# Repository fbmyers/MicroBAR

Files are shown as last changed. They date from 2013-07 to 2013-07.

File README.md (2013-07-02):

MicroBAR
========

This repository contains hardware, firmware, and software revisions to the Microfluidic Bioamplification Reader (MicroBAR) from UC Berkeley.

githalytics.com alpha githalytics.com (http://githalytics.com/fbmyers/MicroBAR)

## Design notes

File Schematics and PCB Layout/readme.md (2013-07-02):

Schematics and PCB Layout
========

Schematic and PCB layout was done in Altium Designer Release 10.

The MicroBAR consists of two PCBs which are stacked on top of one another.  A single header connects these two boards.  "LAMP Microcontroller PCB" contains the microcontroller and all digital electronics, and it sits on the bottom.  "LAMP Chip PCB" contains the phototransistors, amplifier, MUXes, LED driver, and heater driver.  It sits on top.

Board Level Modifications (to be rolled into next revision):
1) A jumper wire was added between 3 and 6 on U4
2) A jumper wire was added between pin 17 on the expansion header and pin 10 on the B2B header
3) Only 3 LEDs were used along the top side of the detection region (the original plans call for 3 on top and 3 on bottom).

There are a number of problems with the SD card wiring:
4) A jumper wire was added between ICSP1 pin 3 and R1 (SD_SCK)
5) A jumper wire was added between ICSP1 pin 4 and R2 (SD_MOSI)
6) A jumper wire was added between ICSP1 pin 1 and U1 pin 25 (SD_MSIO)
7) Pins 1-3 on the SD slot header were wired incorrectly.  To fix this, the CS line going to pin 2 was jumpered to pin 1 and the original trace going to pin 2 was cut.  The MOSI line going to pin 3 was jumpered to pin 2 and the original trace going to pin 3 was cut.  And pin 3 was jumpered to ground.

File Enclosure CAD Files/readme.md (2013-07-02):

Enclosure CAD Files
========

The enclosure was designed in Rhinocerous 4, exported to STL, and printed on a ZPrint 3D printer.

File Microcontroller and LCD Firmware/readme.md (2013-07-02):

Microcontroller and LCD Firmware
========

Firmware is based on the Arduino 1.0.4 Platform.  The "controller.ino" is the main sketch.  The MicroBAR hardware is based on the Arduino Mega 2560 platform.  The LCD is the Amulet MK-480272C color touchscreen LCD module, which itself features a built-in graphics environment that is programmed with modified HTML/CSS/Javascript.  The Amulet GEMcompiler 1.1.2 was used to compile the HTML files and download them onto the LCD module.

The Atmega 2560 chip must first be programmed with the Arduino Bootloader and the Atmega 8U2 must be programmed with the DFU USB firmware (both using the ICSP headers on the board and an AVR-ISP module).  Then the system will behave as an Arduino and the firmware sketches may be uploaded via USB.  A customized DFU firmware (which identifies itself as "Berkeley MicroBAR 2", rather than "Arduino Mega 2560", is available here.  The bootloader can be installed via the Arduino IDE.

Note that not all hardware features are currently implemented in firmware.

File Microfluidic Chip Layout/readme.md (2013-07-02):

Microfluidic Chip Layout
========

The microfluidic chip was designed in AutoCAD 2012.  Darkfield mylar transparencies were printed (from Fineline Imaging) and SU8/silicon molds were fabricated using standard techniques.  The chamber height (circles) was 200 um while the channel height was 10 um.  The PDMS was poured to a height of 4mm.  See the supplementary info in the PLOS ONE paper for more fabrication details.

This version of the microfluidic disposable cartridge features reaction chambers that are 2mm in diameter.  Although we use 2mm chambers in the paper, 1.5mm would probably be sufficient and would load much faster.  Note that the pitch of the chip is 4.5mm (same as a 384 well plate).

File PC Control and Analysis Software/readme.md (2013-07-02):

PC Control and Analysis Software
========

The Processing UI is based on processing-1.2.1.  This is the main control software for the MicroBAR, and it exposes all of the MicroBAR's current functionality (the LCD UI is not fully-functional).

The Windows driver is identical to the Arduino Mega 2560 driver except the device name has been changed.  

The MATLAB Analysis Scripts parse the log files generated by the Arduino, perform background subtraction and smoothing functions, and generate output graphs.  Future versions of this should combine the MATLAB functionality into the control UI.

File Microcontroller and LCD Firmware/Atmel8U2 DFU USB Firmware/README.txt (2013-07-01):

Arduino Uno and Mega 2560 Firmwares for the ATmega8U2

This directory contains the firmwares used on the ATmega8U2 on the Arduino
Uno and Arduino Mega 2560.  The arduino-usbdfu directory contains the DFU
bootloader on the 8U2; the arduino-usbserial directory contains the actual
usb to serial firmware.  Both should be compiled against LUFA 100807.  The
two .hex files in this directory combine the dfu and serial firmwares into
a single file to burn onto the 8U2.  

To burn (Uno):

avrdude -p at90usb82 -F -P usb -c avrispmkii -U flash:w:UNO-dfu_and_usbserial_combined.hex -U lfuse:w:0xFF:m -U hfuse:w:0xD9:m -U efuse:w:0xF4:m -U lock:w:0x0F:m

To burn (Mega 2560):

avrdude -p at90usb82 -F -P usb -c avrispmkii -U flash:w:MEGA-dfu_and_usbserial_combined.hex -U lfuse:w:0xFF:m -U hfuse:w:0xD9:m -U efuse:w:0xF4:m -U lock:w:0x0F:m

(note: MicroBAR-dfu_and_usbserial_combined.hex is exactly the same as MEGA except the name has been changed to "Berkeley MicroBAR 2")

Note on USB Vendor IDs (VID) and Product IDs (PID): The arduino-usbdfu
project uses Atmel's VID and MCU-specific PIDs to maintain compatibility
with their FLIP software.  The source code to the arduino-usbserial
project includes Atmel's VID and a PID donated by them to LUFA.  This
PID is used in LUFA's USBtoSerial project, which forms the basis for
arduino-usbserial.  According to the LUFA documentation, this VID/PID
combination is:

 "For use in testing of LUFA powered devices during development only,
 by non-commercial entities. All devices must accept collisions on this
 VID/PID range (from other in-development LUFA devices) to be resolved
 by using a unique release number in the Device Descriptor. No devices
 using this VID/PID combination may be released to the general public."

The production version of the arduino-usbserial firmware uses the
Arduino VID.  This is only for use with official Arduino hardware and
should not be used on other products.

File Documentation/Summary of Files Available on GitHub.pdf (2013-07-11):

Rev. 2013-06-21

The GitHub repository contains all of the design and source code files for the MicroBAR in their native format. These include:

Schematics and PCB Layout
Software: Altium Designer 10
1. LAMP Chip PCB.PrjPCB
2. LAMP Microcontroller PCB.PrjPCB

This folder includes two separate projects for the two boards in the MicroBAR:

Microcontroller and LCD Firmware
Software: Adruino 1.0.4 and Amulet Technologies GEMcompiler 1.1.2.
1. Amulet LCD GUI. The "mainmenu.htm" is the root page that should be downloaded to the LCD. Atmel8U2 DFU USB Firmware. This should be programmed onto the 8U2 USB interface chip via AVR-ISP.

2.

Arduino Sketches. These include the firmware code for the MicroBAR. The "controller.ino" is the root sketch. Code for hardware peripherals (LCD, Header, Lights, GPS, etc.) is included in separate sketch files.

3.

This folder includes:

Enclosure CAD Files
Software: Rhinoceros 4
This folder includes the original enclosure design (enclosure.3dm) as well as exported STL files for 3D printing.

PC Control and Analysis Software
Software: Processing 1.2.1 and MATLAB

Windows Driver. Once the 8U2 firmware is loaded, Windows will be able to use this driver to communicate with the MicroBAR as a serial port.

1.

Processing UI. This is the main control program for the MicroBAR, written in the Processing language. LAMP_UI.pde is the main file.

2.

MATLAB Analysis Scripts. All analysis and data visualizationwas carried out in MATLAB. plot_data_from_log.m parses log files generated by the Processing UI and generates a series of plots. microbar_calibration.mat includes the sensitivity coefficient matrix for the detector array.

3.

This folder includes:

Microfluidic Chip Layout
Software: AutoCAD 2012
This folder includes the standard chip layout that we use in this manuscript, which features 96 reaction wells at 4.5 mm pitch, with 16 wells connected in parallel to each of 6 inlets.

## Summary of Files Available on GitHub

LAMP Chip Page 1

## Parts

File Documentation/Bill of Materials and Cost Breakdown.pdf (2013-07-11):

System | Board | Designator | Qty | Vendor | Part # | Mfg # | Description | Function | Unit Price (proto) | Unit Price (>5000) | Ext Price (proto) | Ext price (>5000)
ITO Heater | Top | U1 | 1 Digikey | CLA324-ND | LCA717S | RELAY OPTOMOS 2A SPST-NO 6-SMD | Heater Relay | 6.18 | 2.575 | 6.18 | 2.575
ITO Heater | Top | U7 | 1 Digikey | 296-23551-1-ND | TPS61085PWR IC STEP-UP DC-DC CONV 8-TSSOP | Heater boost converter | 3.33 | 1.283 | 3.33 | 1.283
ITO Heater | Top | C9,C11,C12 | 3 Digikey | 10uF (1206) | input/output filter caps | 0.15 | 0.02 | 0.45 | 0.06
ITO Heater | Top | C10 | 1 Digikey | 1uF (1206) | output filter cap | 0.15 | 0.02 | 0.15 | 0.02
ITO Heater | Top | C13 | 1 Digikey | 100nF (1206) | 0.15 | 0.02 | 0.15 | 0.02
ITO Heater | Top | C14 | 1 Digikey | 2.2nF (1206) | 0.15 | 0.02 | 0.15 | 0.02
ITO Heater | Top | R4 | 1 Digikey | 150k (1206) | 0.05 | 0.01 | 0.05 | 0.01
ITO Heater | Top | R5 | 1 Digikey | 18.2k (1206) | 0.05 | 0.01 | 0.05 | 0.01
ITO Heater | Top | R6 | 1 Digikey | 15k (1206) | 0.05 | 0.01 | 0.05 | 0.01
ITO Heater | Top | R7 | 1 Digikey | 1k (1206) | Half bridge for thermistor | 0.05 | 0.01 | 0.05 | 0.01
ITO Heater | Top | L3 | 1 Digikey | 490-5270-1-ND | LQH55PN6R8NR0LINDUCTOR POWER 6.8UH 1450MA 2220 | 6.8uH heater inductor | 0.44 | 0.172 | 0.44 | 0.172
ITO Heater | Top | D97 | 1 Digikey | 641-1255-1-ND | CDBA120SL-G | DIODE SCHOTTKY 1A 20V SMA | heater diode | 0.82 | 0.209 | 0.82 | 0.209
ITO Heater | Top | RT1 | 1 Digikey | 615-1043-ND | PPG102A1RD | DETECTOR RTD TF 1K OHM +/-0.06% | Thermistor | 18.5 | 2.06 | 18.5 | 2.06
ITO Heater | Top | RT1 | 1 Digikey | 455-1719-ND | S2B-PH-K-S(LF)(SN) CONN HEADER PH SIDE 2POS 2MM | header for thermistor | 0.1 | 0.047 | 0.1 | 0.047
ITO Heater | Top | RT1 | 1 Digikey | 455-1165-ND | PHR-2 | CONN HOUSING PH 2POS 2MM WHITE | 2-pin housing for thermistor | 0.05 | 0.024 | 0.05 | 0.024
ITO Heater | Top | RT1 | 2 Digikey | 455-2148-1-ND | SPH-002T-P0.5L CONN TERMINAL 28-24AWG TIN | JST PH pins | 0.027 | 0.013 | 0.054 | 0.026
ITO Heater | Top | RT1 | 1 Digikey | MC06G-300-ND | 3365/06 300SF CABLE 6 COND 300FT FLAT GRAY | 2-conductor ribbon cable (3 inches) | 0.01 | 0.01 | 0.01 | 0.01
ITO Heater | Top | 1 Delta Tech | CB-50IN-S205 | CB-50IN-S205 | 5-15 ohm, 50x75x0.5mm ITO slides | Heater | 20 | 5 | 20 | 5
ITO Heater | Top | 1 Ace HW | Brass Bar Stock | Heater Contacts | 0.5 | 0.25 | 0.5 | 0.25
ITO Heater | Top | 1 Fry's | Electrically-conductive Epoxy | Heater Contacts | 0.2 | 0.1 | 0.2 | 0.1
ITO Heater | Top | 1 Ace HW | Thermally-conductive Epoxy | Glue for Thermistor | 0.05 | 0.05 | 0
TOTAL: | 51.334 | 11.916
LED Driver | Top | U6 | 1 Digikey | 576-3041-1-ND | MIC3289-24YD6 TRIC LED DRIVR WHITE BCKLGT TSOT-6 | LED booster | 1.9 | 0.973 | 1.9 | 0.973
LED Driver | Top | C6 | 1 Digikey | 10uF (1206) | 0.15 | 0.02 | 0.15 | 0.02
LED Driver | Top | C7 | 1 Digikey | 1uF (1206) | 0.15 | 0.02 | 0.15 | 0.02
LED Driver | Top | C8 | 1 Digikey | 478-6028-1-ND | 06033D334KAT2ACAP CER .33UF 25V X5R 0603 (sub w/ 1206) | 0.33uF | 0.45 | 0.126 | 0.45 | 0.126
LED Driver | Top | R3 | 1 Digikey | P12.4CCT-ND | ERJ-6ENF12R4V RES 12.4 OHM 1/8W 1% 0805 SMD | current sense resistor | 0.07 | 0.005 | 0.07 | 0.005
LED Driver | Top | L2 | 1 Digikey | 490-5271-1-ND | LQH55PN100MR0LINDUCTOR POWER 10UH 1250MA 2220 | 10uH LED inductor | 0.44 | 0.172 | 0.44 | 0.172
LED Driver | Top | P3 | 1 Digikey | 455-1719-ND | S2B-PH-K-S(LF)(SN) CONN HEADER PH SIDE 2POS 2MM | header for leds | 0.1 | 0.047 | 0.1 | 0.047
LED Driver | Top | P3 | 1 Digikey | 455-1165-ND | PHR-2 | CONN HOUSING PH 2POS 2MM WHITE | 2-pin housing for leds | 0.05 | 0.024 | 0.05 | 0.024
LED Driver | Top | P3 | 2 Digikey | 455-2148-1-ND | SPH-002T-P0.5L CONN TERMINAL 28-24AWG TIN | JST PH pins | 0.027 | 0.013 | 0.054 | 0.026
LED Driver | Top | P3 | 1 Digikey | MC06G-300-ND | 3365/06 300SF CABLE 6 COND 300FT FLAT GRAY | 2-conductor ribbon cable (3 inches) | 0.01 | 0.01 | 0.01 | 0.01
LED Driver | Top | P3 | 3 Digikey | P14150CT-ND | LNJ923W8CRA1 LED BLUE SIDE VIEW SMD | Blue LEDs | 0.57 | 0.229 | 1.71 | 0.687
LED Driver | Top | 1 Ace HW | Liquid Electrical Tape | Optical shielding | 0.05 | 0.02 | 0.05 | 0.02
TOTAL: | 5.134 | 2.13
Phototransistor Array | Top | D1-D96 | 96 Digikey | 475-1268-1-ND | SFH 3710-3/4-Z PHOTOTRANSISTOR ALS SMD CHIPLED | Phototransistors | 0.563 | 0.483 | 54.048 | 46.368
Phototransistor Array | Top | U2,U4,U5 | 3 Digikey | ADG732BSUZ-ND | ADG732BSUZ | IC MULTIPLEXER 32X1 48TQFP | MUXes | 12.13 | 6.062 | 36.39 | 18.186
Phototransistor Array | Top | U3 | 1 Digikey | AD8603AUJZREEL7CT-NDAD8603AUJZ-REEL7IC OPAMP GP R-R CMOS TSOT23-5 | transimpedance opamp | 2.07 | 0.797 | 2.07 | 0.797
Phototransistor Array | Top | C4 | 1 Digikey | 10pF | fb capacitor | 0.15 | 0.02 | 0.15 | 0.02
Phototransistor Array | Top | C5 | 1 Digikey | 10pF - not necessary? | input capacitor | 0 | 0 | 0 | 0
Phototransistor Array | Top | R1 | 1 Digikey | 1M | fb resistor | 0.1 | 0.01 | 0.1 | 0.01
Phototransistor Array | Top | R2 | 1 Digikey | 1G - not necessary? | input resistor | 0 | 0 | 0 | 0
Phototransistor Array | Top | R100-101 | 2 Digikey | 1M | bias resistors | 0.1 | 0.01 | 0.2 | 0.02
Phototransistor Array | Top | 1 McMaster | 8647K108 | Neoprene/EPDM/SBR, Soft, 1/16" Thick, 42" Width | black foam | 0.04 | 0.04 | 0.04 | 0.04
Phototransistor Array | Top | 1 McMaster | 7769T88 (#89) | Light Filters 20" X 24" Sheet | "Moss Green" gel #89 | 0.16 | 0.16 | 0.16 | 0.16
TOTAL: | 93.158 | 65.601
Microcontroller | Bot | U1 | 1 Digikey | ATMEGA2560-16AU-NDATMEGA2560-16AUIC AVR MCU 256K 16MHZ 100TQFP | microcontroller | 17.97 | 11.251 | 17.97 | 11.251
Microcontroller | Bot | C1 | 1 Digikey | 22pF (1206) | cap on reset line | 0.15 | 0.02 | 0.15 | 0.02
Microcontroller | Bot | C2-3 | 2 Digikey | 478-3735-1-ND | 08051A200JAT2ACAP CERM 20PF 5% 100V NP0 0805 | xtal caps | 0.23 | 0.038 | 0.46 | 0.076
Microcontroller | Bot | C4-7 | 4 Digikey | 100nF (1206) | decoupling caps | 0.15 | 0.02 | 0.6 | 0.08
Microcontroller | Bot | R4 | 1 Digikey | 10k (1206) | res on reset line | 0.1 | 0.01 | 0.1 | 0.01
Microcontroller | Bot | R8 | 1 Digikey | 1M (1206) | res on xtal | 0.1 | 0.01 | 0.1 | 0.01
Microcontroller | Bot | R11 | 1 Digikey | 27 ohm (1206) | res on xtal | 0.1 | 0.01 | 0.1 | 0.01
Microcontroller | Bot | Y1 | 1 Digikey | XC1282CT-ND | ECS-160-20-5PX-TRCRYSTAL 16.00MHZ 20PF SMD | xtal | 0.56 | 0.25 | 0.56 | 0.25
Microcontroller | Bot | R9-10 | 2 Digikey | 10k (1206) | pullups on PD1/PD0 | 0.1 | 0.01 | 0.2 | 0.02
Microcontroller | Bot | P1 | 1 Digikey | 609-3218-ND | 67996-406HLF | CONN HEADER 6POS .100 STR TIN | ICSP1 header | 0.43 | 0 | 0.43 | 0
TOTAL: | 20.67 | 11.727
USB Interface | Bot | U5 | 1 Digikey | ATMEGA8U2-AU-ND | ATMega8U2-AU MCU AVR 8K FLASH 16MHZ 32TQFP | usb controller | 3.7 | 2.352 | 3.7 | 2.352
USB Interface | Bot | C16-17 | 2 Digikey | 478-3735-1-ND | 08051A200JAT2ACAP CERM 20PF 5% 100V NP0 0805 | xtal caps | 0.23 | 0.038 | 0.46 | 0.076
USB Interface | Bot | R25 | 1 Digikey | 1M (1206) | res on xtal | 0.1 | 0.01 | 0.1 | 0.01
USB Interface | Bot | R26 | 1 Digikey | 27 ohm (1206) | res on xtal | 0.1 | 0.01 | 0.1 | 0.01
USB Interface | Bot | Y2 | 1 Digikey | XC1282CT-ND | ECS-160-20-5PX-TRCRYSTAL 16.00MHZ 20PF SMD | xtal | 0.56 | 0.25 | 0.56 | 0.25
USB Interface | Bot | R24 | 1 Digikey | 10k (1206) | pullup on reset line | 0.1 | 0.01 | 0.1 | 0.01
USB Interface | Bot | R29-30 | 2 Digikey | 22 ohm (1206) | USB data line resistors | 0.1 | 0.01 | 0.2 | 0.02
USB Interface | Bot | Z1-2 | 2 Digikey | F2594CT-ND | PGB1010603MR SUPPRESSOR ESD 24VDC 0603 SMD | USB data line ESD protection | 0.74 | 0.196 | 1.48 | 0.392
USB Interface | Bot | L2 | 1 Digikey | 490-1038-1-ND | BLM21AG121SN1DFERRITE CHIP 120 OHM 200MA 0805 | ESD protection inductor | 0.33 | 0.039 | 0.33 | 0.039
USB Interface | Bot | P10 | 1 Digikey | 609-1039-ND | 61729-0010BLF CONN RCPT USB TYPE B R/A PCB | USB-B port | 1.29 | 0.474 | 1.29 | 0.474
USB Interface | Bot | C18 | 1 Digikey | 100nF (1206) | 0.15 | 0.01 | 0.15 | 0.01
USB Interface | Bot | C19 | 1 Digikey | 1uF (1206) | 0.15 | 0.01 | 0.15 | 0.01
USB Interface | Bot | R27-28 | 2 Digikey | 1k (1206) | TX/RX pullups | 0.1 | 0 | 0.2 | 0
USB Interface | Bot | D7-8 | 2 Digikey | 67-1046-ND | SSL-LX2573GD | LED 2X5MM RECTANGULAR GREEN DIFF | TX/RX LEDs | 0.37 | 0 | 0.74 | 0
USB Interface | Bot | R31-32 | 2 Digikey | 1k (1206) | data line resistors | 0.1 | 0.01 | 0.2 | 0.02
USB Interface | Bot | C20 | 1 Digikey | 100nF (1206) | reset DTR line cap | 0.15 | 0.02 | 0.15 | 0.02
USB Interface | Bot | P8 | 1 Digikey | 609-3218-ND | 67996-406HLF | CONN HEADER 6POS .100 STR TIN | ICSP2 header | 0.43 | 0 | 0.43 | 0
USB Interface | 1 Digikey | Q361-ND | 3021001-03 | CBL USB A-B CON 3' 28/28 AWG | 3' USB cable | 3.15 | 1.23 | 3.15 | 1.23
TOTAL: | 13.49 | 4.923
SD Card Reader | Bot | P9 | 1 Digikey | 478-5063-1-ND | 145738009302859+CONNECTOR SD CARD W/BOSS | SD card slot | 4.7 | 2.916 | 4.7 | 2.916
SD Card Reader | Bot | R33-34 | 2 Digikey | 10k (1206) | card detect / write protect pullups | 0.1 | 0.01 | 0.2 | 0.02
SD Card Reader | Bot | R1-3 | 3 Digikey | 1.8k (1206) | SD level shifter res | 0.1 | 0.01 | 0.3 | 0.03
SD Card Reader | Bot | R5-7 | 3 Digikey | 3.3k (1206) | SD level shifter res | 0.1 | 0.01 | 0.3 | 0.03
SD Card Reader | Bot | U3 | 1 Digikey | 296-18479-1-ND | LP2985A-33DBVRIC LDO REG 3.3V 150MA SOT23-5 | 3.3V regulator | 0.84 | 0.276 | 0.84 | 0.276
SD Card Reader | Bot | C12 | 1 Digikey | 1uF (1206) | input cap for 3.3v reg | 0.15 | 0.02 | 0.15 | 0.02
SD Card Reader | Bot | C13 | 1 Digikey | 2.2uF(1206) | output cap for 3.3v reg | 0.15 | 0.02 | 0.15 | 0.02
SD Card Reader | 1 Amazon | 512MB SD Card | 6 | 3 | 6 | 3
TOTAL: | 12.64 | 6.312
Cell Module | Bot | P11 | 1 Digikey | 255-2997-1-ND | AXK5F60547YG CONN SOCKET BRD/BRD .5MM 60POS | 60-pin socket for cell module | 6.79 | 3.514 | 6.79 | 3.514
Cell Module | Bot | P12 | 1 Digikey | WM3291CT-ND | 473880001 1.90MM SIM CARD READER CONN | SIM card socket | 1.51 | 0.986 | 1.51 | 0.986
Cell Module | Bot | U6 | 1 Digikey | 1016-1243-5-ND | SPX29302T5-L | IC REG LDO ADJ 3A TO263-5 | 3.8V 3A regulator | 2.68 | 1.123 | 2.68 | 1.123
Cell Module | Bot | R15 | 1 Digikey | 22k | 3.8V voltage set res | 0.1 | 0.01 | 0.1 | 0.01
Cell Module | Bot | R16 | 1 Digikey | 10k | 3.8V voltage set res | 0.1 | 0.01 | 0.1 | 0.01
Cell Module | Bot | C8 | 1 Digikey | 478-1777-1-ND | TPSD107K010R0100 CAP TANT LOESR 100UF 10V 10% SMD | output cap for 3.8V reg | 1.13 | 0.36 | 1.13 | 0.36
Cell Module | Bot | C9 | 1 Digikey | 0.1uF | output cap for 3.8V reg | 0.15 | 0.02 | 0.15 | 0.02
Cell Module | Bot | R17 | 1 Digikey | 10k | pullup for boot res | 0.1 | 0.01 | 0.1 | 0.01
Cell Module | Bot | P7 | 1 Digikey | 455-1722-ND | S5B-PH-K-S(LF)(SN) CONN HEADER PH SIDE 5POS 2MM | 5-pin JST PH header for cell phone spkr/mic | 0.2 | 0 | 0.2 | 0
Cell Module | Bot | 1 Digikey | 455-1163-ND | PHR-5 | CONN HOUSING PH 5POS 2MM WHITE | 5-pin housing - for mic/spkr cable | 0.07 | 0 | 0.07 | 0
Cell Module | Bot | 1 Sparkfun | CEL-09533 | GSM/GPRS Module - SM5100B | SM5100B Cell Module | 59.95 | 47.96 | 59.95 | 47.96
Cell Module | Bot | 1 Sparkfun | CEL-00675 | Quad-band Cellular Duck Antenna SMA | Cell Antenna | 7.95 | 6.39 | 7.95 | 6.39
Cell Module | Bot | 1 | Prepay SIM card | 0 | 0 | 0 | 0
TOTAL: | 80.73 | 60.383
GPS Module | Bot | P4 | 1 Digikey | 455-1721-ND | S4B-PH-K-S(LF)(SN) CONN HEADER PH SIDE 4POS 2MM | 6-pin JST header for GPS | 0.17 | 0.076 | 0.17 | 0.076
GPS Module | Bot | P4 | 1 Digikey | 455-1396-ND | SHR-06V-S | CONN HOUSING SH 6POS 1MM WHITE | housing for GPS connector | 0.11 | 0.049 | 0.11 | 0.049
GPS Module | Bot | P4 | 6 Digikey | 455-2148-1-ND | SPH-002T-P0.5L CONN TERMINAL 28-24AWG TIN | JST PH pins | 0.027 | 0.013 | 0.162 | 0.078
GPS Module | Bot | P4 | 1 Digikey | MC06G-300-ND | 3365/06 300SF CABLE 6 COND 300FT FLAT GRAY | 6-cond 28 awg ribbon (3 inches) | 0.03 | 0.03 | 0.03 | 0.03
GPS Module | Bot | P4 | 1 Digikey | 455-1396-ND | SHR-06V-S | CONN HOUSING SH 6POS 1MM WHITE | 6-pin JST housing - GPS end | 0.11 | 0.049 | 0.11 | 0.049
GPS Module | Bot | P4 | 1 Digikey | 455-1561-1-ND | SSH-003T-P0.2 CONN TERM SH CRIMP 28-32AWG TIN | JST SH pins | 0.049 | 0.032 | 0.049 | 0.032
GPS Module | 1 Sparkfun | GPS-00465 | 20 Channel EM-406A SiRF III Receiver with Antenna | GPS module | 59.95 | 47.96 | 59.95 | 47.96
TOTAL: | 60.581 | 48.274
5V Power Supply | Bot | U4 | 1 Digikey | LT1308ACS8#PBF-ND LT1308ACS8#PBFIC DC/DC CONV SINGLE CELL 8-SOIC | 5V, 1A regulator | 6.5 | 3.634 | 6.5 | 3.634
5V Power Supply | Bot | C11 | 1 Digikey | 478-3911-1-ND | TAJC476M010RNJCAP TANTALUM 47UF 10V 20% SMD | 5V booster input cap | 0.46 | 0.147 | 0.46 | 0.147
5V Power Supply | Bot | C15 | 1 Digikey | 22nF (1206) | 0.15 | 0.02 | 0.15 | 0.02
5V Power Supply | Bot | C14 | 1 Digikey | 478-3061-1-ND | TPSD227M006R0100 CAP TANT LOESR 220UF 6.3V 20%SMD | 5V booster output cap | 3.5 | 1.12 | 3.5 | 1.12
5V Power Supply | Bot | R23 | 1 Digikey | 47k (1206) | 0.1 | 0.01 | 0.1 | 0.01
5V Power Supply | Bot | R21 | 1 Digikey | 309k (1206) | 0.1 | 0.01 | 0.1 | 0.01
5V Power Supply | Bot | R22 | 1 Digikey | 100k (1206) | 0.1 | 0.01 | 0.1 | 0.01
5V Power Supply | Bot | L1 | 1 Digikey | 490-5269-1-ND | LQH55PN4R7NR0LINDUCTOR POWER 4.7UH 1750MA 2220 | 5V booster inductor | 0.44 | 0.172 | 0.44 | 0.172
5V Power Supply | Bot | D6 | 1 Digikey | 10BQ015PBFCT-ND | 10BQ015TRPBF DIODE SCHOTTKY 15V 1A SMB | 5V booster diode | 1.02 | 0.336 | 1.02 | 0.336
TOTAL: | 12.37 | 5.459
LiPo Battery/USB Charger | Bot | U2 | 1 Digikey | MCP73831T-2ATI/OTCT-ND MCP73831T-2ATI/OT IC CONTROLLR LI-ION 4.2V SOT23-5 | lipo charger | 0.68 | 0.42 | 0.68 | 0.42
LiPo Battery/USB Charger | Bot | D4 | 1 Digikey | 67-1050-ND | SSL-LX2573YD | LED 2X5MM RECTANGULAR YEL DIFF | charging LED (yellow) | 0.28 | 0.08 | 0.28 | 0.08
LiPo Battery/USB Charger | Bot | R19 | 1 Digikey | 1k (1206) | charging LED res | 0.1 | 0.01 | 0.1 | 0.01
LiPo Battery/USB Charger | Bot | R18 | 1 Digikey | 2k (1206) | current selector for charging IC | 0.1 | 0.01 | 0.1 | 0.01
LiPo Battery/USB Charger | Bot | F1 | 1 Digikey | 507-1075-1-ND | C1Q 500 | FUSE 500MA 125V 1206 FAST C1Q | 500mA USB charging fuse | 0.55 | 0.142 | 0.55 | 0.142
LiPo Battery/USB Charger | Bot | F2 | 1 Digikey | 507-1082-1-ND | C1Q 3 | 3A fuse | 3A battery fuse | 0.55 | 0.142 | 0.55 | 0.142
LiPo Battery/USB Charger | Bot | C10 | 1 Digikey | 478-3934-1-ND | TAJD475M035RNJCAP TANTALUM 4.7UF 35V 20% SMD | lipo charger cap | 0.97 | 0.35 | 0.97 | 0.35
LiPo Battery/USB Charger | Bot | P2 | 1 Digikey | 455-1704-ND | B2B-PH-K-S(LF)(SN) CONN HEADER PH TOP 2POS 2MM | battery connector | 0.1 | 0.0476 | 0.1 | 0.0476
LiPo Battery/USB Charger | Bot | P2 | 1 Sparkfun | PRT-08484 | 6Ah LiPo battery w/ JST connector | battery (many options for this) | 39.95 | 31.96 | 39.95 | 31.96
LiPo Battery/USB Charger | Bot | 2 | screws/brackets for mounting battery | 0.1 | 0.1 | 0.2 | 0.2
TOTAL: | 43.48 | 33.3616
Touchscreen LCD | P3 | 1 Digikey | 455-1721-ND | S4B-PH-K-S(LF)(SN) CONN HEADER PH SIDE 4POS 2MM | header for LCD | 0.17 | 0.076 | 0.17 | 0.076
Touchscreen LCD | P3 | 1 Digikey | 455-1164-ND | PHR-4 | CONN HOUSING PH 4POS 2MM WHITE | 4-pin housing | 0.07 | 0.03 | 0.07 | 0.03
Touchscreen LCD | P3 | 4 Digikey | 455-2148-1-ND | SPH-002T-P0.5L CONN TERMINAL 28-24AWG TIN | JST PH pins | 0.027 | 0.013 | 0.108 | 0.052
Touchscreen LCD | P3 | 1 Digikey | MC06G-300-ND | 3365/06 300SF CABLE 6 COND 300FT FLAT GRAY | 4-cond 28 awg ribbon | 0.02 | 0.02 | 0.02 | 0.02
Touchscreen LCD | 1 Digikey | 681-1018-ND | MK-480272C | KIT COLOR MODULE 480X272 TFT | 4.3" Color LCD Touchscreen | 223.44 | 50 | 223.44 | 50
TOTAL: | 223.808 | 50.178
General | Bot | D1,D2 | 2 Digikey | 67-1047-ND | SSL-LX2573ID | LED 2X5MM RECTANGULAR RED DIFF | Status LEDs (red) | 0.37 | 0.079 | 0.74 | 0.158
General | Bot | D5 | 1 Digikey | 67-1046-ND | SSL-LX2573GD | LED 2X5MM RECTANGULAR GREEN DIFF | power LED (grn) | 0.37 | 0.074 | 0.37 | 0.074
General | Bot | R12,R13,R20 | 3 Digikey | 1k (1206) | Resistors for status/power LEDs | 0.1 | 0.01 | 0.3 | 0.03
General | Bot | S1 | 1 Digikey | 401-1223-ND | F2UEE | SWITCH PB DPDT ALT ACT SILVER | power switch | 2.32 | 1.036 | 2.32 | 1.036
General | Bot | S1 | 1 Digikey | 401-1221-ND | F1204 | SW CAP RECT GREY 5.5MM ACT | power switch gray cap | 1.05 | 0.355 | 1.05 | 0.355
General | Bot | B1 | 1 Digikey | 458-1066-ND | PK-12N40PQ | BUZZER PIEZO 4.1KHZ 14MM PC MT | Buzzer | 2.43 | 1.978 | 2.43 | 1.978
General | Bot | P6 | 1 Digikey | WM8129-ND | 90131-0131 | CONN HEADER 22POS .100" STR TIN | 2x11 expansion header | 2.36 | 0 | 2.36 | 0
General | Top | P1 | 1 Digikey | 609-3220-ND | 67996-416HLF | CONN HEADER 16POS .100 STR TIN | 2x8 male board 2 board header | 0.83 | 0.277 | 0.83 | 0.277
General | Bot | P5 | 1 Digikey | WM4241-ND | 901512116 C-GRID PCB CONN DR VT TN-A 16CKT | 2x8 female board 2 board header | 3.24 | 1.484 | 3.24 | 1.484
General | 4 | standoff | standoffs between boards | 0.3 | 0.1 | 1.2 | 0.4
General | 8 | screws for enclosure | 0.02 | 0.005 | 0.16 | 0.04
General | 1 | black foam for optical shielding in lid | 0.04 | 0.04 | 0.04 | 0.04
TOTAL: | 15.04 | 5.872
Manufacturing | 1 Adv. Ckits | PCB Fabrication | 66 | 10 | 66 | 10
Manufacturing | 1 Adv. Ckits | PCB Assembly (SMT soldering) | 130.6 | 53.96 | 130.6 | 53.96
Manufacturing | 1 | 3D printed enclosure (low quant) | 10 | 10 | 0
Manufacturing | 1 QuickParts | Injection molded enclosure (high quant) | 2.5 | 0 | 2.5
Manufacturing | 1 | Assembly & Testing (low quant, 4 hr @ $20/hr) | 80 | 80 | 0
Manufacturing | 1 | Assembly & Testing (high quant, 2hr @ $5/hr) | 10 | 0 | 10
TOTAL: | 286.6 | 76.46
| Prototype | >5000
FULL BOX TOTAL NO LCD/GPS/CELL | 919.035 553.916 | 382.5966 223.7616

## MicroBAR v.2 Bill of Materials

Manufacturing Totals

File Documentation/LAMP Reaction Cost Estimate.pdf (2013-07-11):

Reaction Volume: | 6.28E-07 L
Reaction Cost: | 0.012893607
Cost/uL: | 0.020531221
Cost/chip | 1.237786242

Solids
Reagent | Molecular Weight | Mass (g) | Moles | Cost | Cost/mole | Concentration/Rea | Moles/reaction | Cost/reaction | Fraction of Cost
Tris Buffer | 127.2 | 100 | 0.786163522 | $74 | 94.128 | 0.02 | 1.256E-08 | 1.18225E-06 | 0.01%
KCl | 74.55 | 500 | 6.706908115 | $31 | 4.59228 | 0.01 | 6.28E-09 | 2.88395E-08 | 0.00%
MgSO4.7H2O | 246.47 | 500 | 2.02864446 | $30 | 14.7882 | 0.008 | 5.024E-09 | 7.42959E-08 | 0.00%
(NH4)2SO4 | 132.14 | 100 | 0.756773119 | $14 | 18.76388 | 0.01 | 6.28E-09 | 1.17837E-07 | 0.00%
MnCl2 | 197.91 | 100 | 0.505280178 | $22 | 43.93602 | 0.001 | 6.28E-10 | 2.75918E-08 | 0.00%
Calcein | 622.53 | 5 | 0.008031741 | $103 | 12761.865 | 0.00005 | 3.14E-11 | 4.00723E-07 | 0.00%

Solutions
Reagent | Concentration (M) | Volume (L) | Moles | Cost | Cost/mole | Rxn Concentration | Moles/reaction | Cost/reaction | Fraction of Cost
Betaine | 5 | 0.0015 | 0.0075 | $20 | 2666.666667 | 0.8 | 5.024E-07 | 0.001339733 | 10.39%
dATP | 0.1 | 0.00025 | 0.000025 | $37 | 1470000 | 0.0014 | 8.792E-10 | 0.001292424 | 10.02%
dCTP | 0.1 | 0.00025 | 0.000025 | $37 | 1470000 | 0.0014 | 8.792E-10 | 0.001292424 | 10.02%
dGTP | 0.1 | 0.00025 | 0.000025 | $37 | 1470000 | 0.0014 | 8.792E-10 | 0.001292424 | 10.02%
dTTP | 0.1 | 0.00025 | 0.000025 | $37 | 1470000 | 0.0014 | 8.792E-10 | 0.001292424 | 10.02%
Bst Polymerase | 8000000 | 0.001 | 8000 | $244 | 0.0305 | 320000 | 0.20096 | 0.00612928 | 47.54%
Tween 20 (%) | 1 | 100 | 100 | $27 | 0.273 | 0.2 | 1.256E-07 | 3.42888E-08 | 0.00%
Primers FIP/BIP | | | 0.0000005 | 45 | 90000000 | 0.0000032 | 2.0096E-12 | 0.000180864 | 1.40%
Primers LoopF/B | | | 0.0000002 | 10 | 50000000 | 0.0000016 | 1.0048E-12 | 0.00005024 | 0.39%
Primers F3/B3 | | | 0.0000002 | 16 | 80000000 | 0.0000004 | 2.512E-13 | 0.000020096 | 0.16%

Reagents are from Sigma or New England Biosciences, Primers are from IDT

MicroBAR LAMP Reaction Cost Estimate

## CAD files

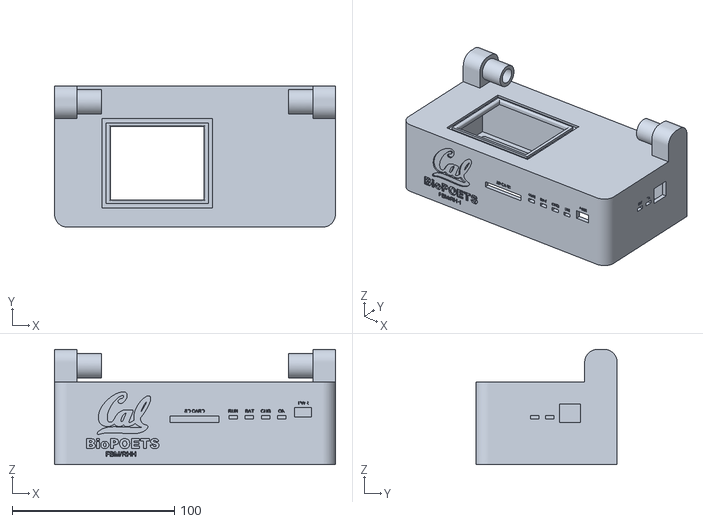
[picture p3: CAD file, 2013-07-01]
Enclosure CAD Files/STL Files/enclosure v1 - body.stl
173.0 x 87.0 x 71.0

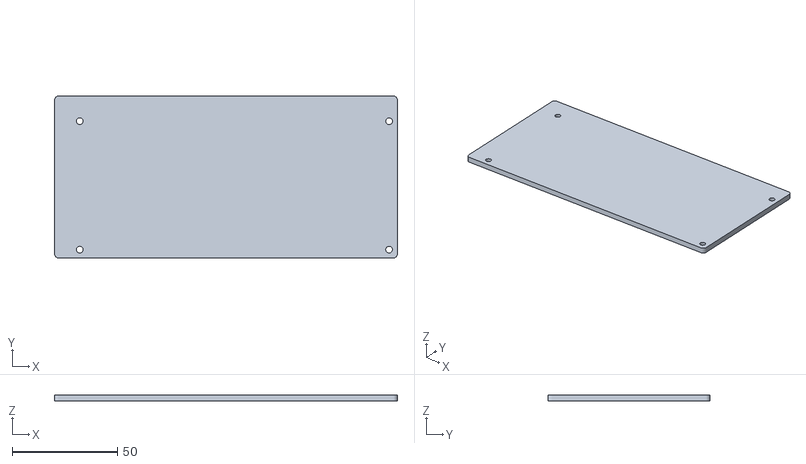
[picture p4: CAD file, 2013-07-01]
Enclosure CAD Files/STL Files/enclosure v1 - bottom plate.stl
163.0 x 77.0 x 3.00

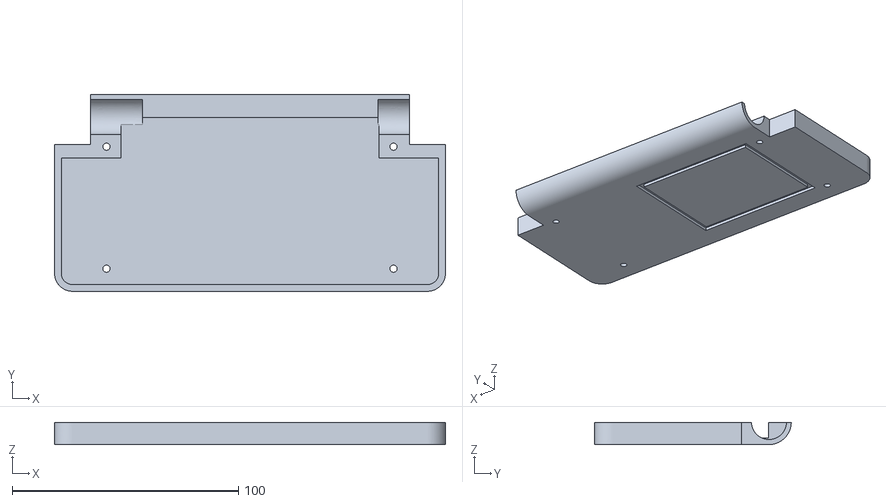
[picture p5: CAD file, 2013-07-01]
Enclosure CAD Files/STL Files/enclosure v1 - lid bottom.stl
173.0 x 87.0 x 9.84

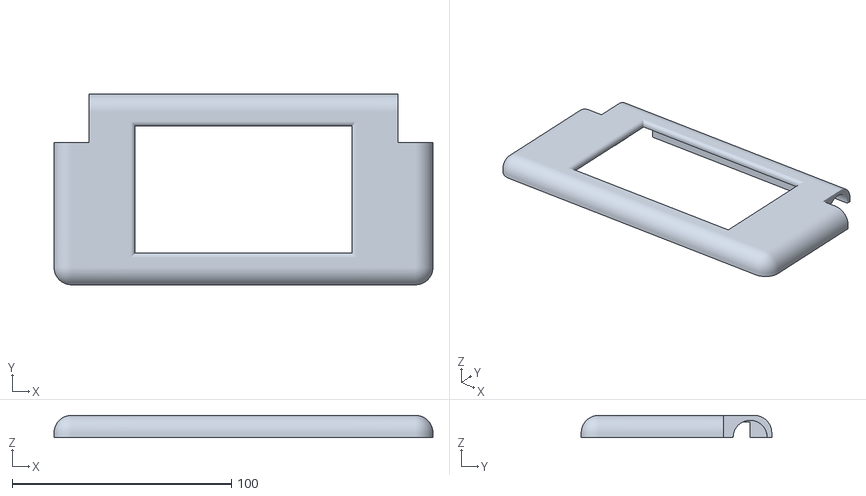
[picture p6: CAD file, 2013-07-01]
Enclosure CAD Files/STL Files/enclosure v1 - lid top.stl
173.0 x 87.0 x 10.2

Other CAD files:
Microfluidic Chip Layout/MicroBAR Chip - 2mm Chambers - V1.dwg
Schematics and PCB Layout/Gerber Files/Chip Reader PCB Top Paste Mask.dxf
Schematics and PCB Layout/Gerber Files/Microcontroller PCB Top Paste Mask.dxf

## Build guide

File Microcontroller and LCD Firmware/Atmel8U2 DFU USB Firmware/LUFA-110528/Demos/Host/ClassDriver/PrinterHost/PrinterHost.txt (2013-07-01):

/** \file
 *
 *  This file contains special DoxyGen information for the generation of the main page and other special
 *  documentation pages. It is not a project source file.
 */

/** \mainpage Printer Host Demo
 *
 *  \section Sec_Compat Demo Compatibility:
 *
 *  The following list indicates what microcontrollers are compatible with this demo.
 *
 *  - Series 7 USB AVRs (AT90USBxxx7)
 *
 *  \section Sec_Info USB Information:
 *
 *  The following table gives a rundown of the USB utilization of this demo.
 *
 *  <table>
 *   <tr>
 *    <td><b>USB Mode:</b></td>
 *    <td>Host</td>
 *   </tr>
 *   <tr>
 *    <td><b>USB Class:</b></td>
 *    <td>Printer Device</td>
 *   </tr>
 *   <tr>
 *    <td><b>USB Subclass:</b></td>
 *    <td>Bidirectional Protocol</td>
 *   </tr>
 *   <tr>
 *    <td><b>Relevant Standards:</b></td>
 *    <td>USBIF Printer Class Specification \n
 *        PCL Language Specification</td>
 *   </tr>
 *   <tr>
 *    <td><b>Usable Speeds:</b></td>
 *    <td>Low Speed Mode \n
 *        Full Speed Mode</td>
 *   </tr>
 *  </table>
 *
 *  \section Sec_Description Project Description:
 *
 *  Printer host demonstration application. This gives a simple reference
 *  application for implementing a USB Printer host, for USB printers using
 *  the bidirectional data encapsulation protocol and PCL language.
 *
 *  Upon connection of a compatible printer, the printer's device ID is sent
 *  to the AVR's serial port, and a simple test page is printed using the PCL
 *  printer language.
 *
 *  \section Sec_Options Project Options
 *
 *  The following defines can be found in this demo, which can control the demo behaviour when defined, or changed in value.
 *
 *  <table>
 *   <tr>
 *    <td>
 *     None
 *    </td>
 *   </tr>
 *  </table>
 */

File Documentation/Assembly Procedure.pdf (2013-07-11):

a. PCBs (order from Advanced Circuits)
b. SMT solder paste stencils (order from Pololu)
c. All components listed in bill of materials
d. Tube of solder paste
e. Trowel (glass slide will also work)
f. Skillet
g. Fine tipped tweezers
h. Tape and scrap PCBs
i. Power supply with a cable to plug into JST battery input connector
j. Conductive epoxy
k. Spray paint and primer
l. 2-part clear epoxy (fast drying)
m. AVR-ISP mkII in-circuit programmer
1. Materials you need:

Each piece is saved as a separate STL file. Load these all simultaneously into the Zprinter software and it should automatically arrange them. You can do a "fix" on the parts if there have been changes.

a.

b. 3D print using default settings
c. After 24 hours or so, remove the parts and epoxy according to directions. Let sit overnight.
2. Printing 3D enclosure

In current version, I drilled pilot holes (no actual tapping) with a #43 bit in the PCB pillars and in the lid. But the material strips easily with these fine threads. In the next version, there shouldn't be any tapping (except maybe the lid). Rather, just use pockets for nuts/4-40 sleeves in the lid and base. So in all places where there should be a nut (8 in the lid and 4 in the base) that is epoxied in.

a.

b. Countersink the heads so the lid closes flat (may also print that directly into future designs)
c. It's good to test fit the components. The display required some tweaking
3. Tapping holes in 3D enclosure
a. Sand the enclosure thoroughly with 100 grit sandpaper
Prime, sand, prime, sand. Be careful of rounding off edges. I applied 2-3 coats of primer, but only a little at a time. So in total I probably sprayed it 8 times with primer, and 8 times with paint, considering I also had to rotate it and get it from all sides.

b.

Spray paint with semi-gloss black. Use thin coats and even strokes. No need to paint the interior, but definitely coat it with primer.

c.

4. Painting 3D enclosure
a. Tape several scrap PCBs to the table around the PCB to be populated so it fits snug without sliding Align and tape the stencil over the PCB. The scrap PCBs are there so the trowel doesn't bow off the edges.

b.

c. Squeeze out *plenty* of solder paste at one end of the board.
With one firm motion, smear the solder paste over the stencil, try to keep it very uniform and get paste in all the holes. Touchup if necessary

d.

e. Remove the stencil with one motion.
Place all the components on the top side of the board. Ensure you've got the correct polarity on things. Most solder paste bridges will fix themselves, if there's not too much solder.

f.

Plug in the skillet and turn it all the way to max. Place the board on the skillet. The warmest region is around the circular heating element.

g.

After about 3 minutes, the paste will begin to reflow. Move the board around a bit if one part isn't getting hot enough. The whole process should take <5 minutes.

h.

5. Populating PCBs (see Sparkfun tutorial on using Skillet for PCB reflow)

Rev. 2013-06-21

## MicroBAR Assembly Procedure

LAMP Chip Page 1

When all the components have reflowed, turn off the skillet and carefully remove the board and set it down to cool.

i.

j. Inspect all components for solder bridges, bad connections, etc.
k. Flip the board over and populate it with a regular tip iron
Populate all through-hole components by hand. If populating the cell phone module, take special care that the 60-pin socket doesn’t have any solder bridges and the module is soldered down to the board securely.

l.

Populate the rectangular LEDs, with special care to bend them at the correct position and solder them at the correct height.

m.

n. Snip off the tip of the pushbutton - this will make assembly easier (only one detent is needed) Note the PCB mods that I made in the "readme.txt" file and make these revisions (mostly adding jumper wires). These should be incorporated into the next version.

o.

Plug a power supply with current limiting capability to the battery in port and turn it all the way down.

a.

Slowly ramp up the voltage on the power supply and make sure there isn't a significant current draw. If there is, you've likely got a solder bridge short.

b.

Set the power supply to 4 V and probe the 5V, 3.8V, and 3.3V supplies on the board to make sure they're correct. Vary the power input and make sure they are stable

c.

Turn off the power supply and connect the top board (screw in the standoffs). Repeat this procedure.

d.

Connect a LiPo battery to the port and connect the USB port to a computer. Verify that the USB port does not overdraw current and that the battery voltage increases steadily (charging) when it is plugged in. Also verify that when you press the power switch, the computer recognizes new hardware (Atmel 8U2)

e.

Dry fit the boards to the 3D enclosure (if available) and make any adjustments to the protruding components, if necessary.

f.

6. Initial testing

Cut brackets out of brass for the cell phone antenna and the LiPo battery. Attach these to the bottom PCB and mount the antenna and battery. There should be a piece of foam between the battery and the bottom of the PCB to prevent the bottom components from digging into the battery.

a.

7. Install battery and cell phone antenna
a. Make sure drivers are installed for the AVR-ISP mkII (easiest way to do this is to install AVR Studio)

Note that this firmware is the same as that available from the Arduino website, but I modified the descriptor string.

i.

Download with:
avrdude -p at90usb82 -F -P usb -c avrispmkii -U flash:w:MicroBAR_dfu_and_usbserial_combined.hex -U lfuse:w:0xFF:m -U hfuse:w:0xD9:m -U efuse:w:0xF4:m -U lock:w:0x0F:m

ii.

b. Connect the AVR-ISP mkII to the ICSP2 header to download the 8U2 DFU firmware.
i. Point Windows to the "Windows Driver" directory and install the driver
c. Make sure the board enumerates as "Berkeley MicroBAR 2"

Plug in the mkII to the ICSP1 header and fire up the Arduino software. Make sure the correct board (Arduino 2560) is selected and correct COM port is selected, then go to "burn bootloader"

d.

e. Unplug the mkII and power cycle the board.
f. Load the Controller.ino software onto the MicroBAR
8. Downloading the AVR firmware (USB controller and Arduino bootloader)
a. When the MicroBAR restarts, you should hear two beeps and see the RUN/BAT lights flash. This indicates that the firmware is running.
b. Open the arduino serial monitor and verify that you get state data from the board. Then run the Processing UI and verify that you see data from the phototransistors and that you can tell the board to run an assay.
9. Firmware testing

Verify that all 96 phototransistors respond individually (block out all but one using black foam and observe that each one is uniquely addressed). If there is a problem, it may indicate a solder bridge on the addressing pins.

c.

a. Start w/ 75x50x0.5mm ITO coated glass slide from Delta Technologies (5-15 ohm/sq)
b. Verify which side is conductive
i. Start w/ ~100um brass bar from Ace HW, 3/4" wide, K&S Engineering 614121102330 ii. Cut to width of slide w/ tin snips (50mm)
iii. Mark 5mm line on one side
iv. Use tin snips to cut the pins (about 1.5mm wide)
v. Put in vice (pins down) and cut at 5mm line using Dremel cut-off wheel
vi. Use wire brush wheel to remove flashing and roughen back side (where epoxy will go) vii. Put in vice and bend legs 90 degrees
viii. Make sure pins will insert into PCB.
c. Cut ITO heater brackets
i. Lay brackes face down on kimwipe
ii. Dry fit slide, make sure spacing is correct, double check for conductive side
iii. Before gluing the slide, put a dot where the thermistor will go (middle of slide ~5mm in)
Mix conductive epoxy and smear on bracket evenly. Cut a small piece of the brass to apply it to the slide.

iv.

Lay slide down (conductive side facing down) and push IN on brackets a bit so excess epoxy goes outside rather than smearing on the slide. Make sure it makes contact along entire length of bracket. Let it sit with a light weight on the slide for 10 minutes or so.

v.

Mix 2-part epoxy (Loctite quickset) and then pickup a small droplet (brass piece works for this) and apply on the slide.

vi.

vii. Use tweezers to place thermistor on slide, in the middle of the droplet
viii. Once glue has set (20 min) transfer to oven (60C) for 1 hr. Or let sit overnight.
d. Glue on brackets and thermistor
10. Assembling ITO heater

Cut (2) 50x75x1mm glass slides and make 2 50x7mm strips to use as waveguides. Best to cut each waveguide from a separate slide.

i.

Use flat black spraypaint, lay waveguides on napkin flat, sandwiched between other glass slides to mask off the regions we don't want to spray paint. Best to use the slides you cut from, so the edge fits perfectly.

ii.

iii. Shake can and spray evenly, lightly so it doesn't drip on the sides
iv. Make sure to get both ends (small ends)
v. Once one side's dry, flip them over and do the other
vi. Use sandpaper if necessary to remove any paint on the clear sides
a. Cut/spraypaint waveguides

Once spraypaint is dry (could put in oven to accelerate this), mix more 2-part epoxy and apply small droplets at the edges of the brackets.

i.

Set the waveguide down on top of the brass brackets. Note that the glass should extend over the ITO a bit (to avoid scattering into the ITO) and should be flush at either end of the brass brackets.

ii.

iii. Let glue dry

b. Glue on waveguides

Use helping hands to hold ITO slide vertically. Make sure the helping hands have lots of tape around them so they don't mark the ITO. Grip it by the brackets (not the waveguide).

i.

ii. Pull out 3 LEDs and line them up in the same orientation (you'll want to get them quickly) iii. Make sure all the polarities are the same (note the position of the green line on the back) Mix more 2-pary epoxy and dip each LED into the epoxy (just barely, don't let the epoxy cover the contacts). Place them on the edge of the glass waveguide, 3 to a side. One should be in

iv.

c. Glue on LEDs
11. Adding LEDs/waveguides the center and the other two should line up so they're between columns 3 and 4 on the chip (use a scrap chip to eyeball it)...or maybe measure this precisely.
v. Once you've done 3, let the glue dry, flip over the ITO, and do the other side.
Make sure the polarities of the other side line up, so a series string around all 6 will have them all in the proper polarity.

vi.

Use soild wire wrap wire (32 awg) and cut small pieces to connect between the LEDs. Bend the ends of the wire at 90 degrees, and solder them on one by one. The end of one side will connect with the beginning of the other.

i.

Use small stranded wire from ribbon cable (28awg) to make a connector tying the strings together and put a JST connector on it (make sure the orientation is correct).

ii.

d. Wire up LEDs

Coat all LEDs/wires with liquid electrical tape and make sure no light can escape, except through the waveguide. Hold the slide such that whichever side you're currently coating is facing down, since the liquid electrical tape tends to drip. 3-4 coats seems to do the trick. Note that this is also strain relief for the leads.

e.

f. Let it dry
Connect leads to thermistor. Use smallest heatshrink to protect leads from each other, and put a JST connector on the other end.

g.

Plug in the ITO, thermistor, and LEDs and test them using the software. Check to make sure the ITO is getting hot, the LEDs can vary their brightness across all the levels, and the thermistor is reading approximately the correct temperature. The ITO should have approximately 10V across it. The LEDs should not flicker.

12.

The thinner foam (1/16") is for the insert underneath the ITO, and the thicker foam (1/8") is for the light gasket.

a.

These burn very easily, so cut them on the lowest power setting on the Versalaser (Paper). I used ~ 0.1mm for the 1/16" @ +10% or so, and 1mm @0% for the gasket (both on Paper).

b.

c. Test fit both
13. Cutting foam insert and gasket

Cut green gel to fit array and sandwich this between the ITO and foam. Get the height level and as close as possible to the PTs without the slide touching, then solder down the ITO.

14.

Mix up more epoxy and smear it in the trench on the base, careful to avoid getting it around the sides. Insert the gasket. Do this quickly since the epoxy sets in 5 min. DO NOT put something heavy on the foam while it's drying or it will be permanently compressed.

a.

15. Attaching light gasket

See current design. Antenna bracket is cut from brass, 9mm wide, with a 4-40 hole at one end and a 90 degree bend at the other for the SMA connector to thread through.

a.

Battery bracket should fit between the holes under the board and be a little larger than the battery, so foam will fit snugly in there.

b.

Attach the battery. Use a 4-40 nut/bolt. Cut a square of foam to go between the battery and PCB, and a strip of foam to go along the underside of the bracket.

c.

d. Thread the SMA connector into the bracket.
16. Cutting battery and antenna brackets
a. In this version, the clearances really aren't sufficient. The enclosure should be enlarged slightly. Use a drill bit for 75% thread engagement for 4-40 screws and drill holes in the pillars. Note that this isn't ideal, and you should instead epoxy nuts in the pillars since the 3D printed material is prone to stripping.

b.

Screw in the top board using the mid-size standoffs from Digikey). Put the board in and use a 4-40 screw to actually drive the standoff into the material (let the screw bottom out in the standoff). Then hold the standoff with pliers and back the screw out.

c.

To get the bottom board in, make sure all the LEDs are bent so they will sit just behind the enclosure and bend the board-to-board header towards the hinge side so the pins are at an angle. Then you can wiggle the bottom board in and get it to mate while the USB port protrudes through. Pushing

d.

17. Installing PCBs the switch in the ON position helps.
Screw in 4 more standoffs (same length). Make sure to attach the antenna bracket to one of them. This is what the base will screw in to.

e.

a. Burn LCD firmware on via USB port

Remove RS-232 connector and power connector. I just used angle cutters to cut them apart and then desoldered the pieces from the board

i.

ii. Cut the traces which go to the MAX232 on the board (these are clearly marked)
iii. Solder the TX/RX/+5/GND leads onto the board directly. The wire should be ~8" long
b. Modifications to Amulet LCD

New enclosure version should have pillars for mounting the LCD with embedded 4-40 nuts. So you'll just screw it in. I just cut foam (2 thick pieces) to sandwich the display in. I cut out holes in the foam for all the components on the PCB.

c.

18. Installing LCD module
a. Use double sided tape or hot glue to glue the module into the lid.
b. Make a small JST connector w/ 5 wires coming off it.
c. Attaching lid pieces and verifying that hinge works
Use hot glue to attach the GPS receiver. The LCD can be floating (next version it should fit more snugly).

d.

e. Thread the GPS/LCD cables through the hinge and put the hinge together
f. Screw the hinge together using wood screws (#4, 5x8")
g. Add JST connectors to GPS cable and LCD cable.
h. Plug GPS/LCD into PCB.
19. Installing GPS module

Screw it in using 3/4" 4-40 screws. These should be a little more than finger tight...any more and you will strip out the pillars.

a.

20. Attaching base

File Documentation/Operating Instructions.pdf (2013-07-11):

1) The chip mold is fabricated using standard SU-8 lithography techniques
2) Chips are molded from Sylgard 184 PDMS with a 10:1 curing weight ratio
After molding, remove the chips from the wafer and cut along the edges with a sharp straight razor blade. Note that initially we cut a little beyond the edge of the chip and we make the final edge cut after the "floor" of the chip is bonded.

3)

A 4 mm hole punch is used to create the inlet wells (Harris Unicore, Ted Pella). Make sure to clean the punch with Eliminase.

4)

5) The bottom of the chip is cut from Stockwell Elastomerics .010" Thick HT6240 sheets.
Both the PDMS channels and the "floor" sheet are treated with Eliminase to remove DNA, DNAse, and RNAse and then are rinsed with ultrapure water.

6)

7) The two chip parts are bonded using oxygen plasma.
8) After bonding, the edges are cut to the precise dimensions

Making PDMS Chips

1) Currently, the LAMP reaction mix is prepared off-chip under sterile conditions. Template is added last. Positive and negative reaction mixes are split into two tubes: one for the thermocycler and one for the MicroBAR

2)

3) The MicroBAR cartridge is vacuum treated for > 1 hr prior to loading.
At this point, cartridges may be sealed for future use using a commercial food sealer (although they should be vacuum treated first with a more powerful vacuum as the food sealer isn't powerful enough to enable full vacuum loading).

4)

20 uL of each reaction mix is loaded into each inlet immediately after it is taken out of vacuum. It takes about 30 minutes for the reaction mix to fully load into all chambers.

5)

Setting up a Chip

Make sure you have a fully-charge battery or you have the instrument plugged in to wall power (note that we added a power plug in lieu of the LiPo battery so that the instrument could be powered continuously with a 5V wall-wart power supply. The power supply you use should have a rating of at least 2A.

1)

During powerup, you should see the lights go through all 16 brightness levels, the run and bat lights flash once, and you should hear two beeps.

2)

3) Plug the box into the USB port
4) Fire up the UI
Often, it doesn't connect the first time. Close the UI, unplug the USB and plug it back in again. That almost always fixes it.

5)

The time between samples. Note that internally, the MicroBAR averages 100 samples per sample that it returns.

a. Step time (2000 ms)

The photodetector amplifier needs a little time to reach a steady state value, so we let the instrument run for a certain number of steps before we start recording.

b. Stabilization steps (10)

This determines the length of the assay. Run steps * step time = total assay time (although actually it's a little off due to the way it calculates things).

c. Run steps (5000)

This is the run temperature

d. Temp (60 C)
e. LEDs (1)
6) Set your assay parameters (note that we almost always use the defaults, which are given in parentheses):

Operating the MicroBAR

Rev. 2013-06-21

## MicroBAR Operating Instructions

LAMP Chip Page 1

Sets the light level. These are logarithmically spaced intensity values from 1-15 (0 is OFF, 1 is lowest intensity). Values above 1 tend to saturate the detectors, so we stick with 1.

If you only want to sample a subset of wells, you specify the start and stop here.

f. Start Well (1)

Stop well to sample.

g. End Well (96)

Click "Set Assay Params" and verify that the unit responds with the correct parameters (the unit's state is printed on the right side)

7)

Set the appropriate output directory. Note that it must already exist. Don't include a filename here, that will be automatically added (.log)

8)

Insert chip and line it up with the phototransistors. Make sure that the bottom of the chip sits flat and the PDMS "wets" the surface of the ITO/glass slide. This will ensure that it doesn't flex during heating.

9)

10) Close the lid gently and make sure it completely seals (might have to wiggle it back and forth a bit)
11) Click Start Assay and wait
12) The unit will emit 3 long beeps when it's done
To view the data, load the Matlab script and change the filename to your log file. It takes a long time to parse the log files, but it saves them as a MAT file so you can do this again and it's much faster.

13)

Specify the colors of the wells you want to plot. PLOT_COLORS tells the script what color to print (standard matlab 1-letter abbreviations). If you set a well to 0, it won't print.

14)

LAMP Chip Page 2

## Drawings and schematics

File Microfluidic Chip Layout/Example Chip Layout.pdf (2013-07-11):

### Disposable Microuidic Cartridge Layout

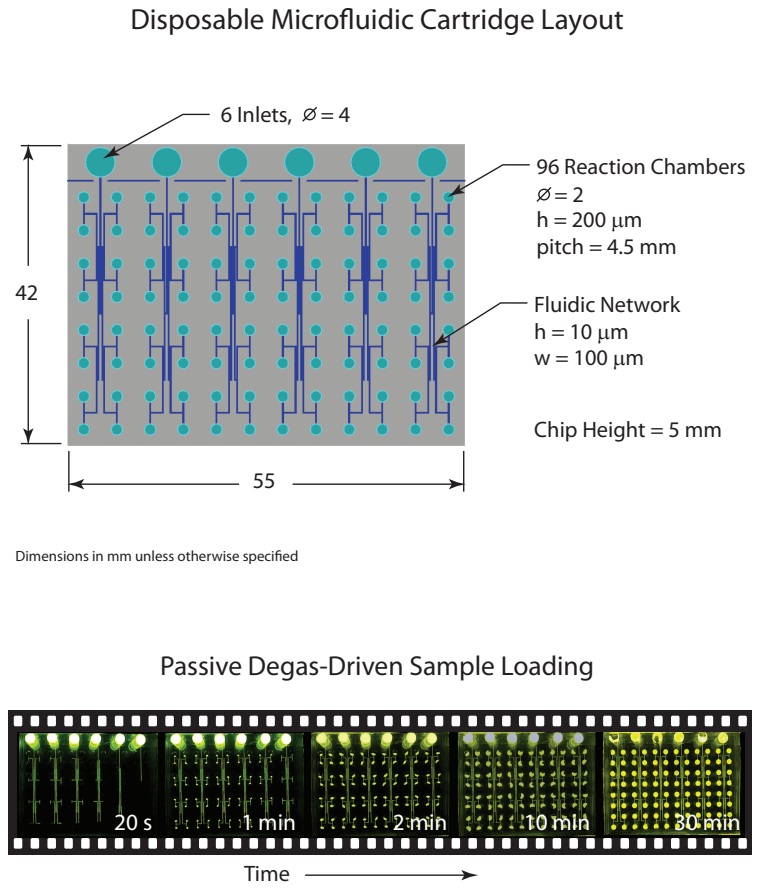
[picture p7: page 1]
6 Inlets, = 4; 96 Reaction Chambers; h = 200 µm pitch = 4.5 mm; Fluidic Network h = 10 µm w = 100 µm; Time; 1 min; 2 min; 10 min; 30 min

Chip Height = 5 mm

Dimensions in mm unless otherwise specied

Passive Degas-Driven Sample Loading

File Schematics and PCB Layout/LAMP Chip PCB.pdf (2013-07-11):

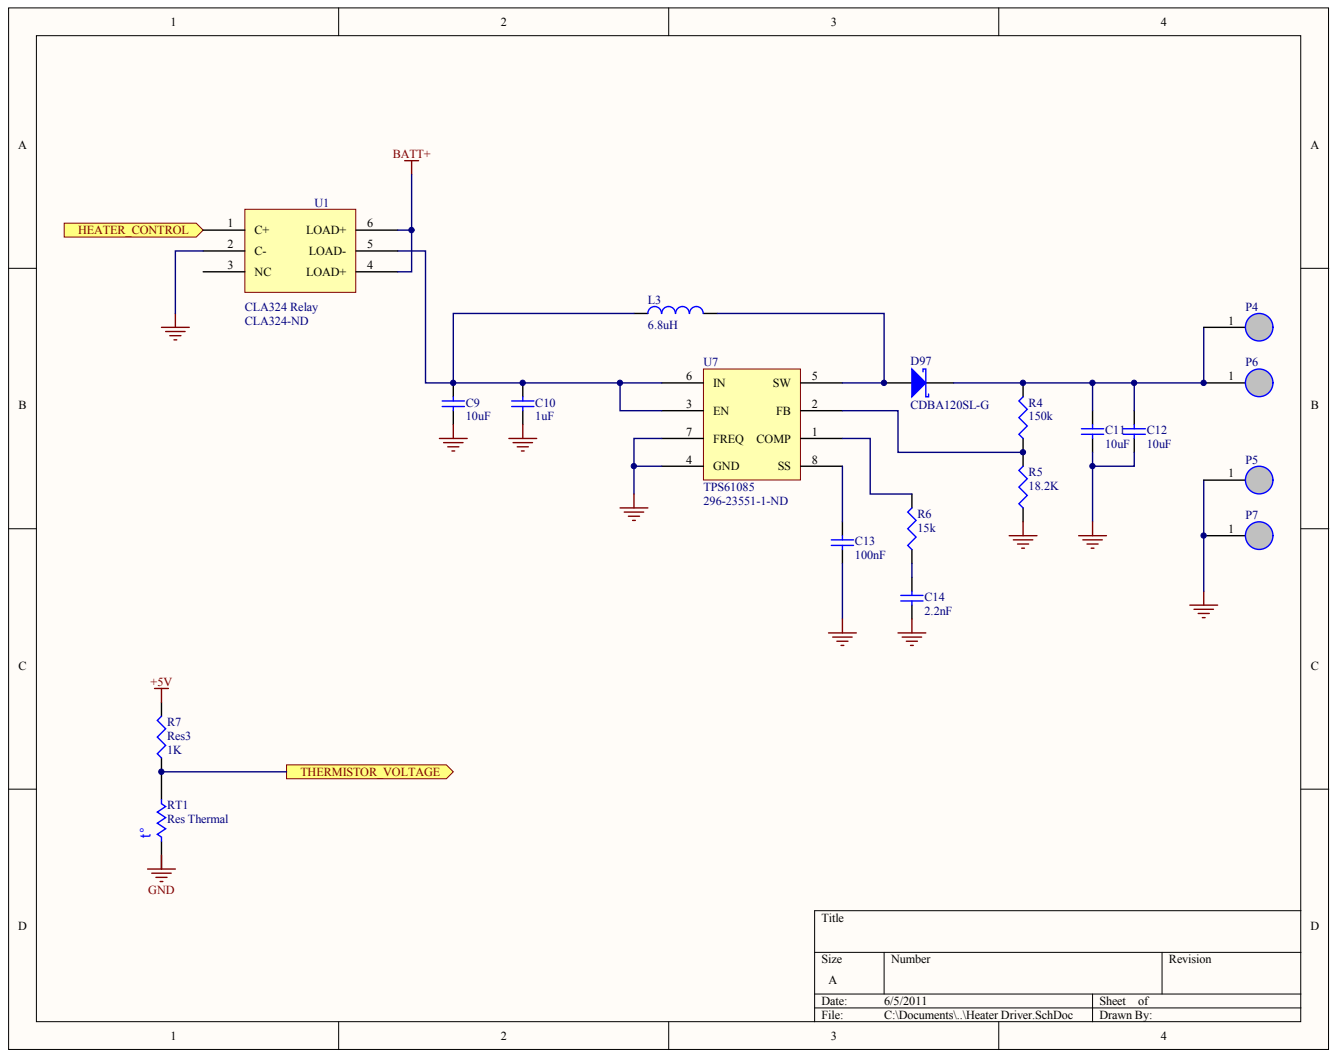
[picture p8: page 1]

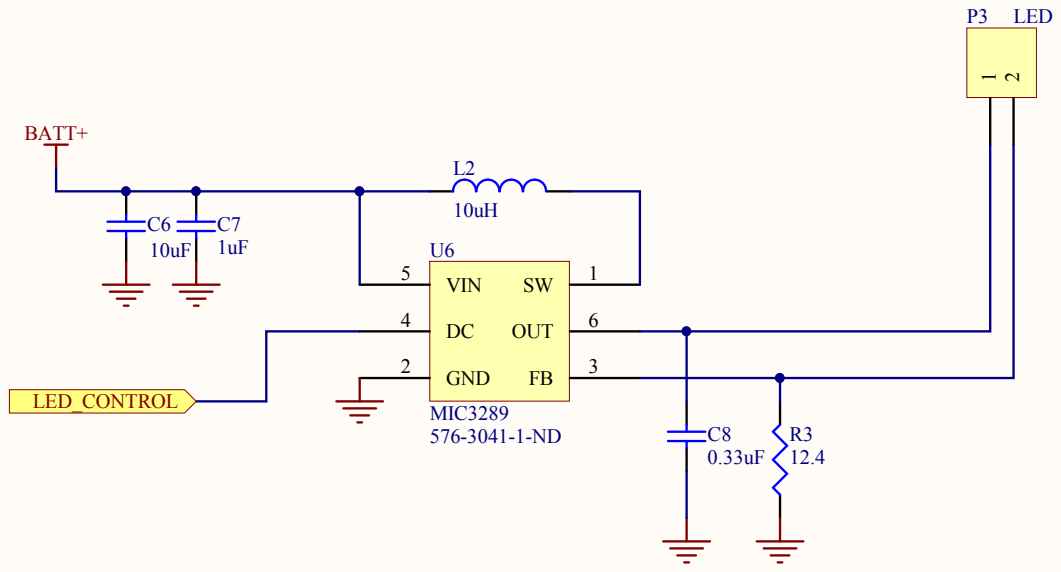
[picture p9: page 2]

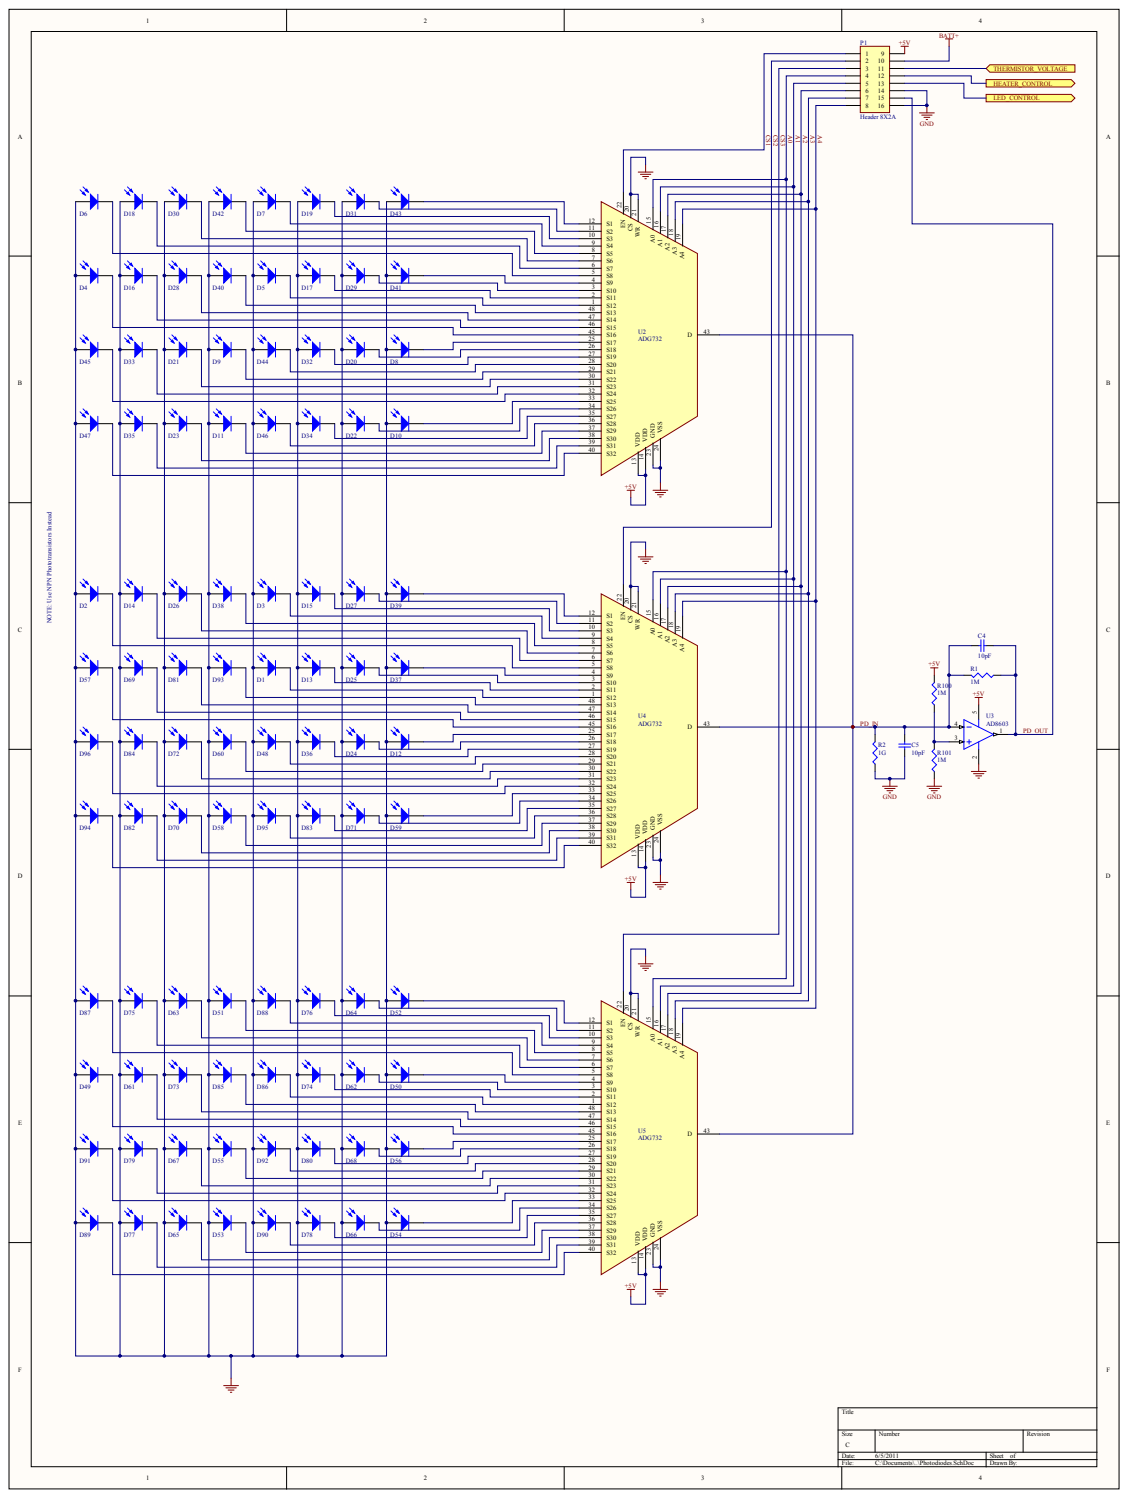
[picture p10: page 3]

NOTE: Use NPN Phototransistors Instead

Size C | Number | Revision

File: C:\Documents\..\Photodiodes.SchDoc | Drawn By:

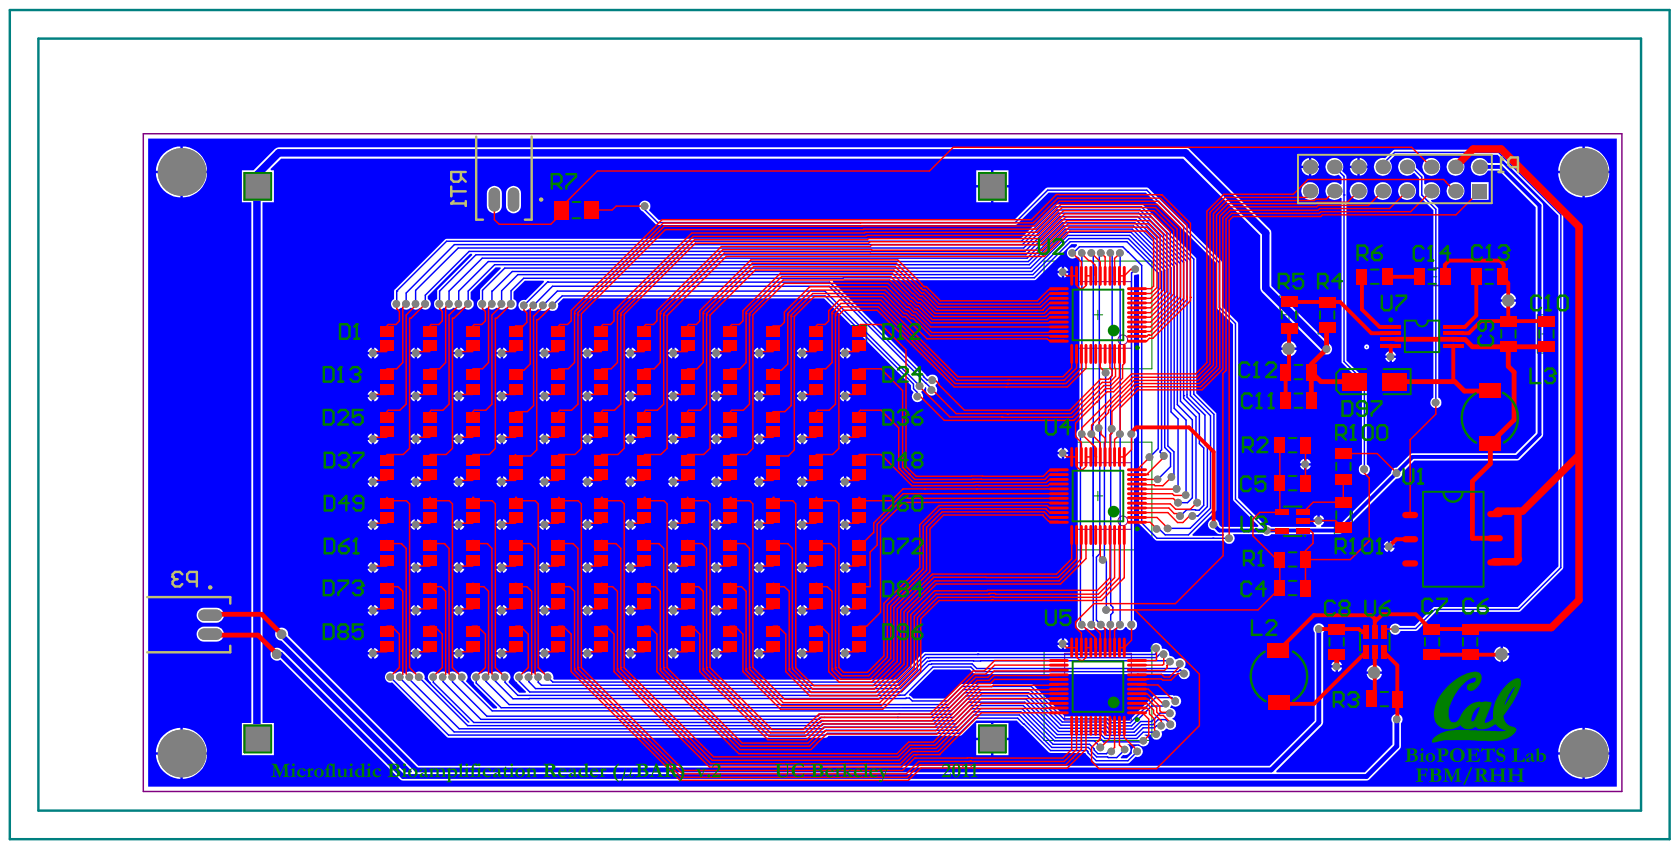
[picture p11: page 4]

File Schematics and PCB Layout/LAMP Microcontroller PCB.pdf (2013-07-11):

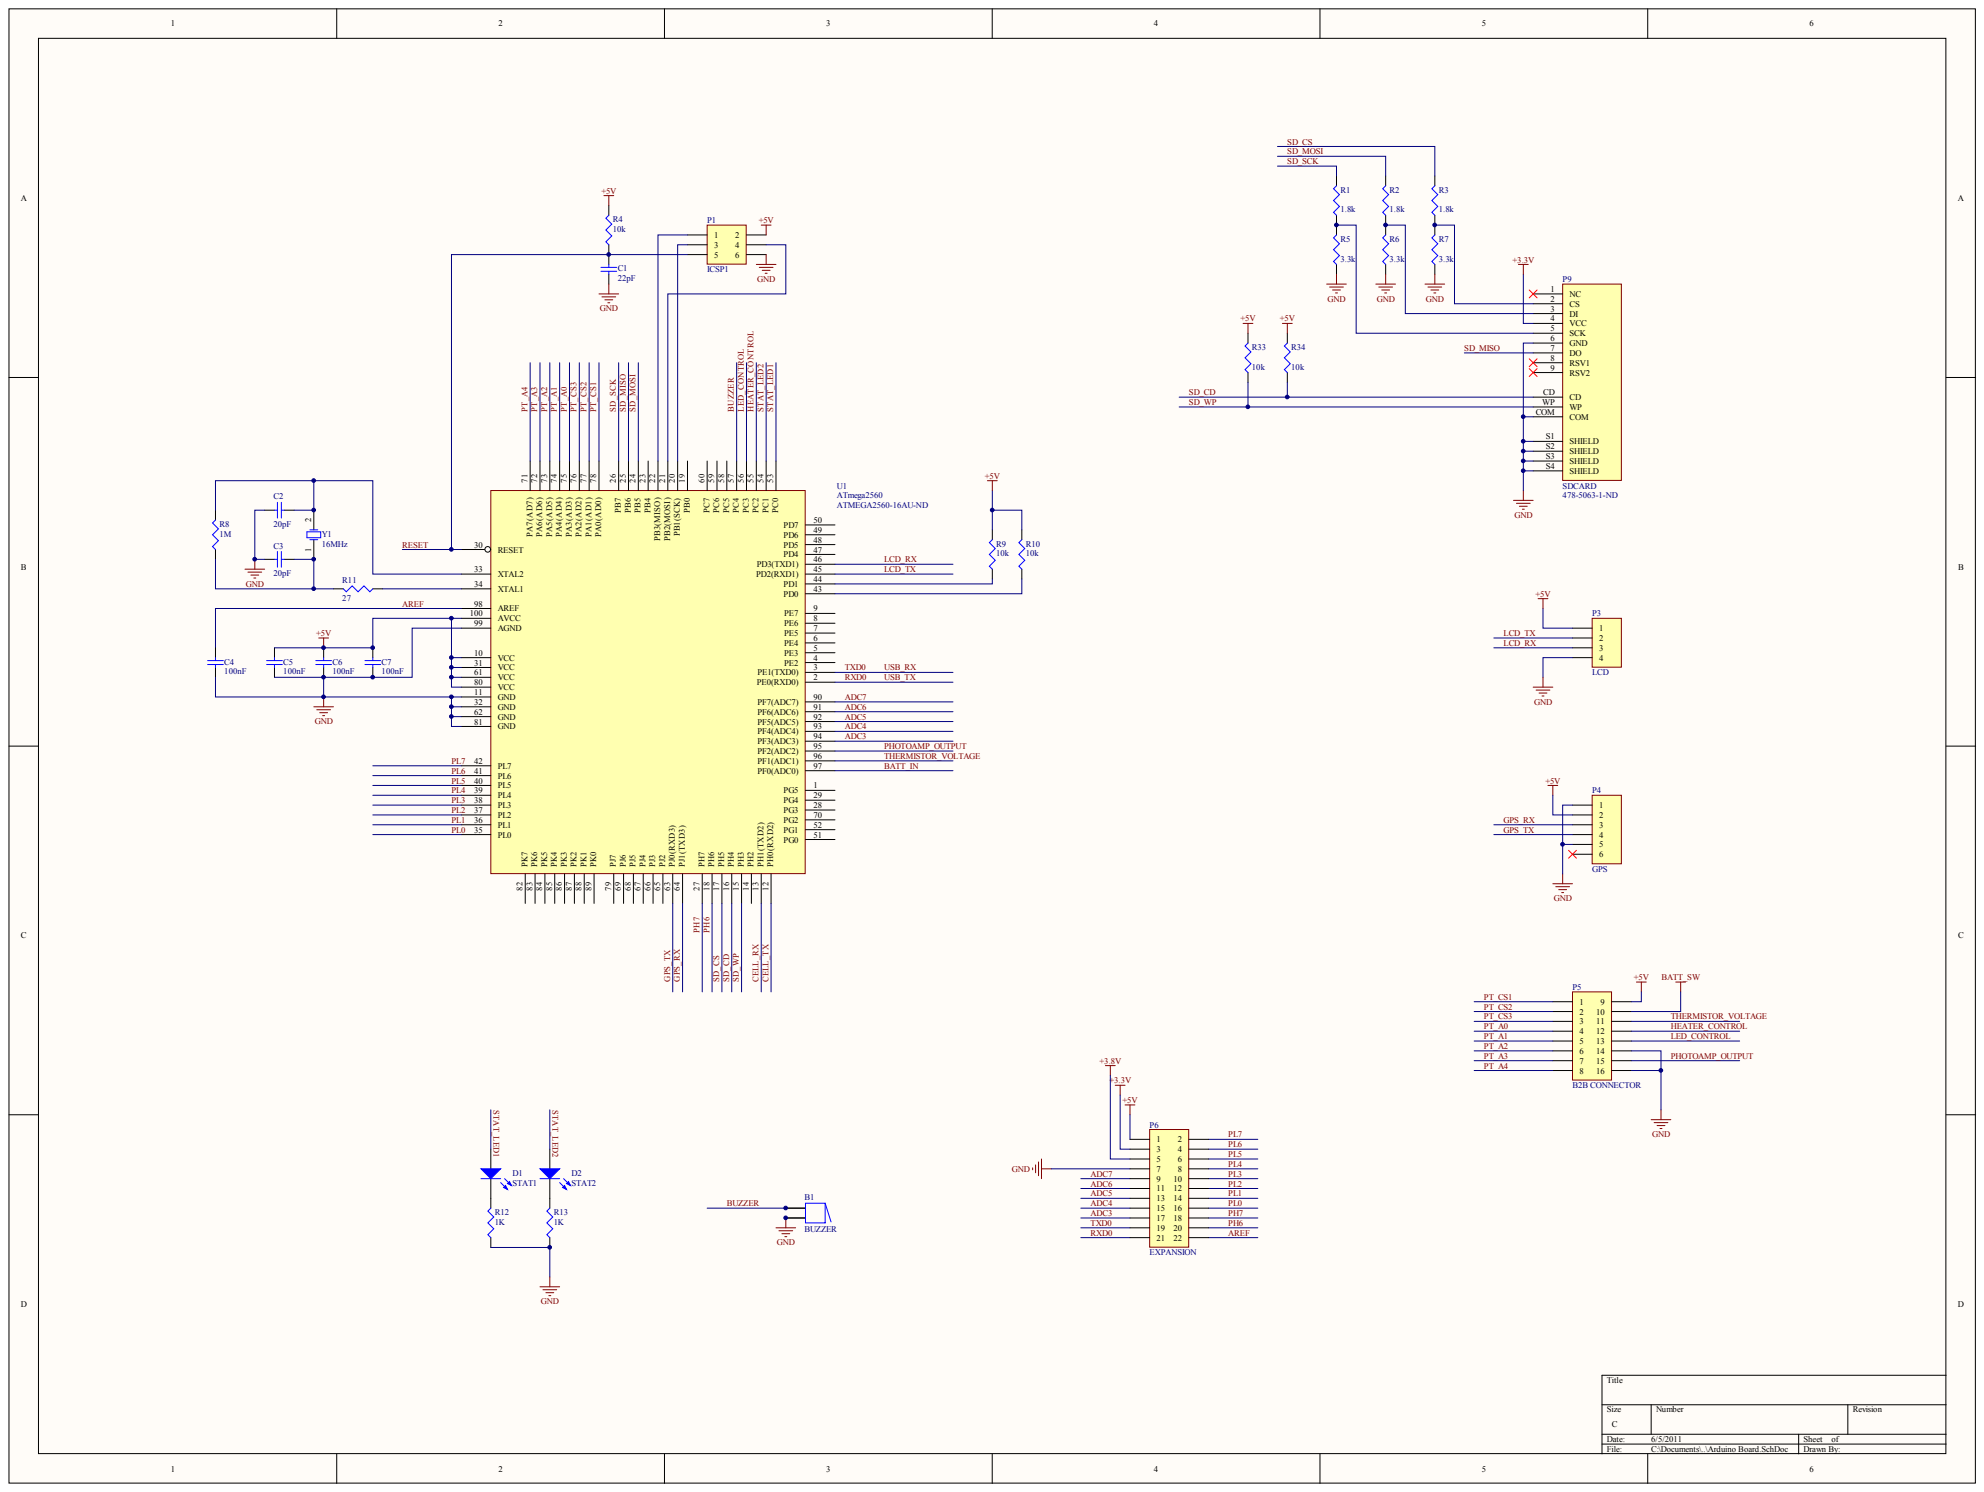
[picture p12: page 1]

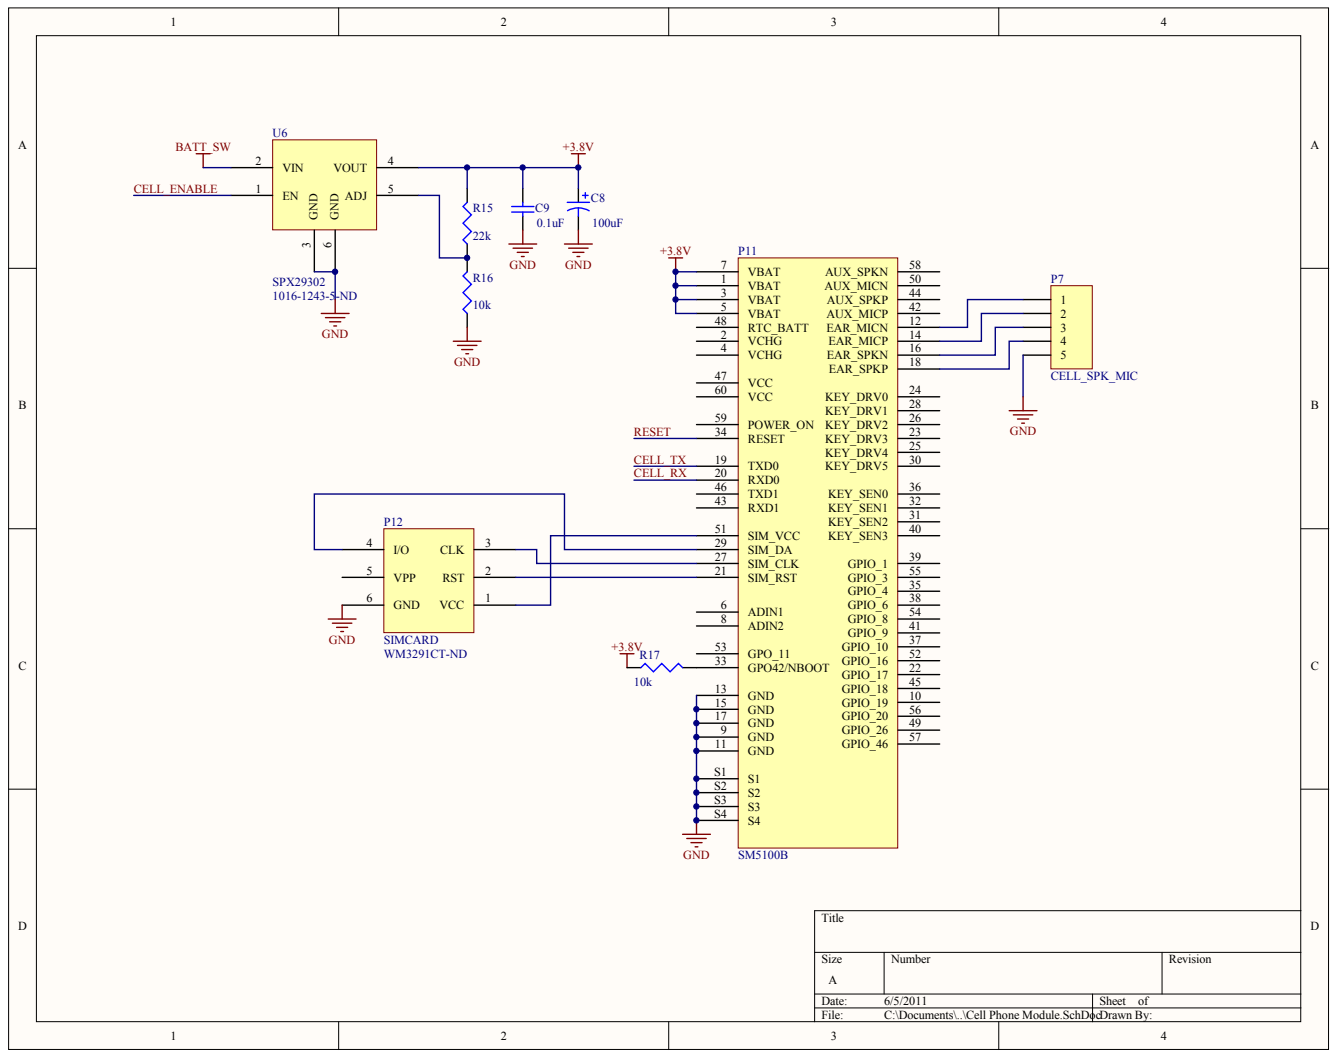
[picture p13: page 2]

SIM_DA 29

SIM_RST 21

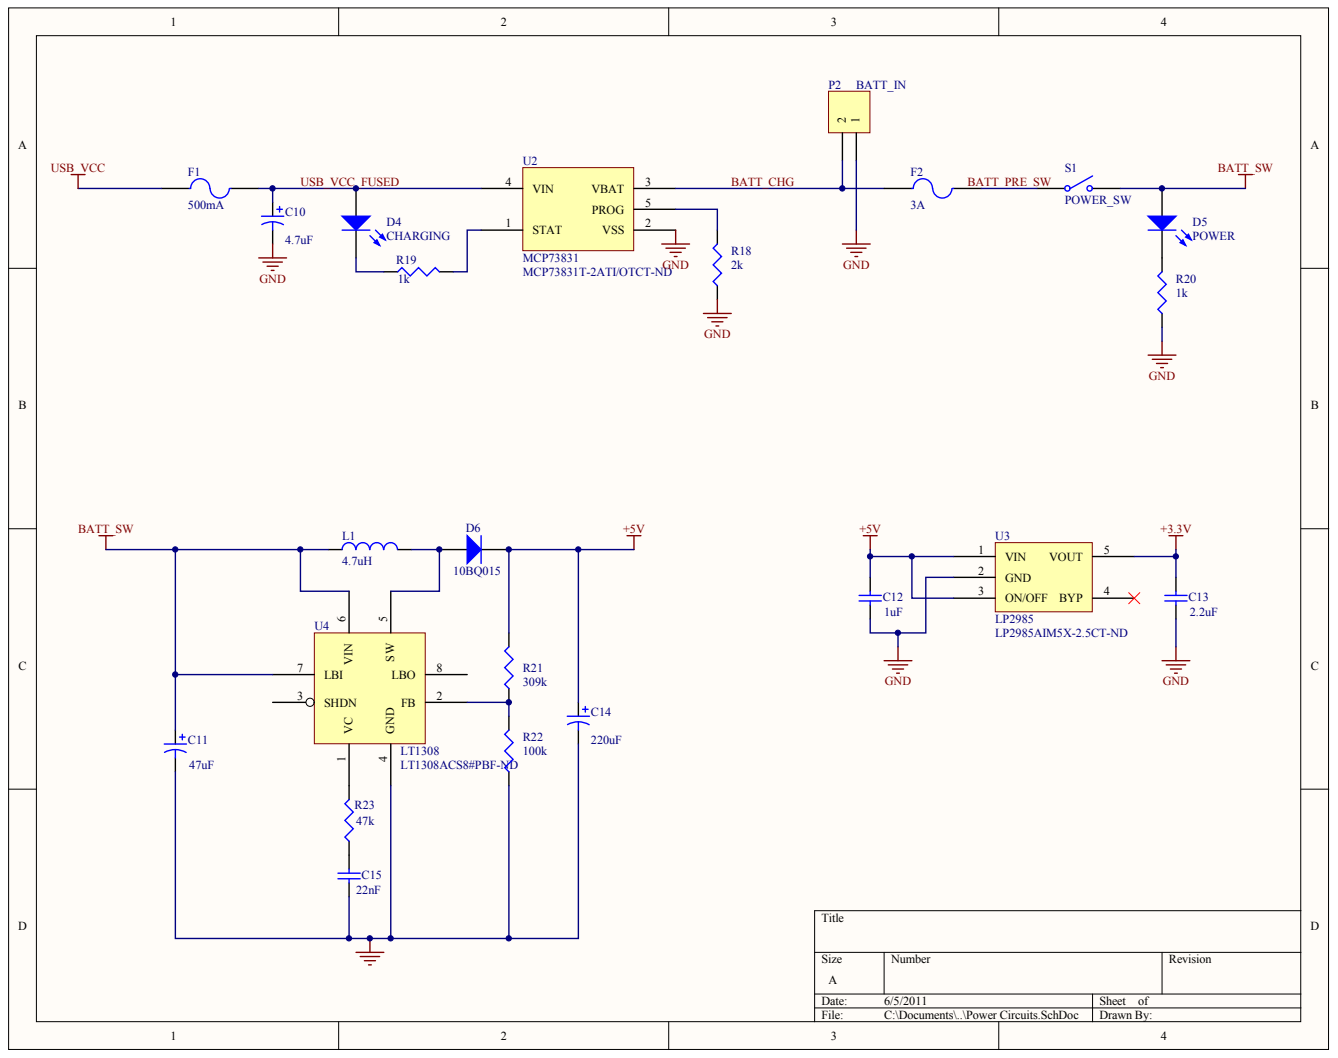
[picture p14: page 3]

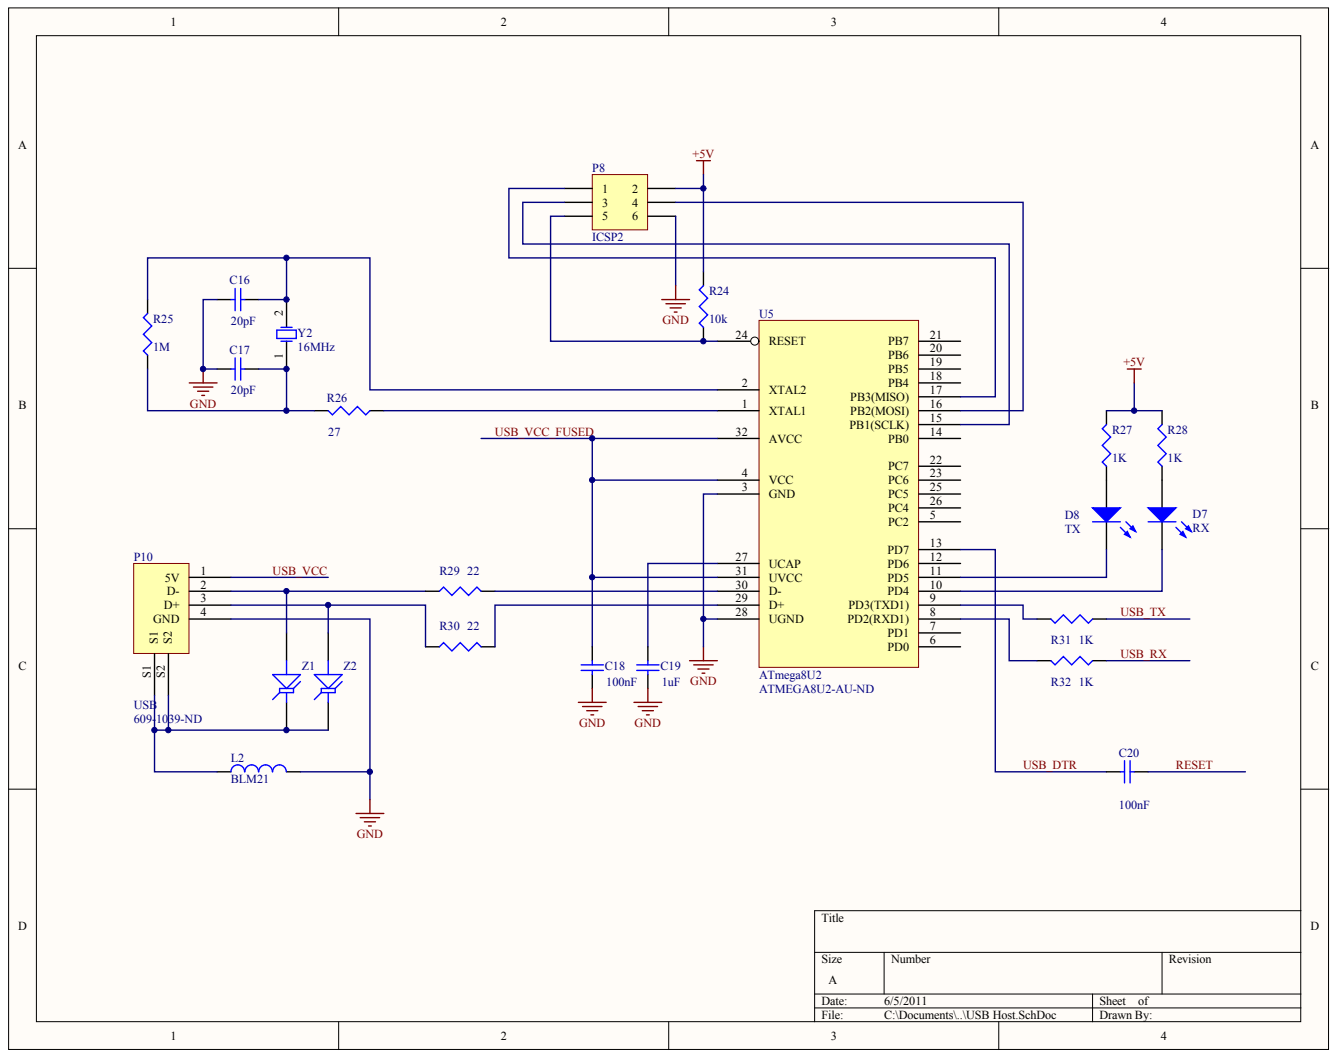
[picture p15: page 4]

XTAL2 2

GND | XTAL1 1

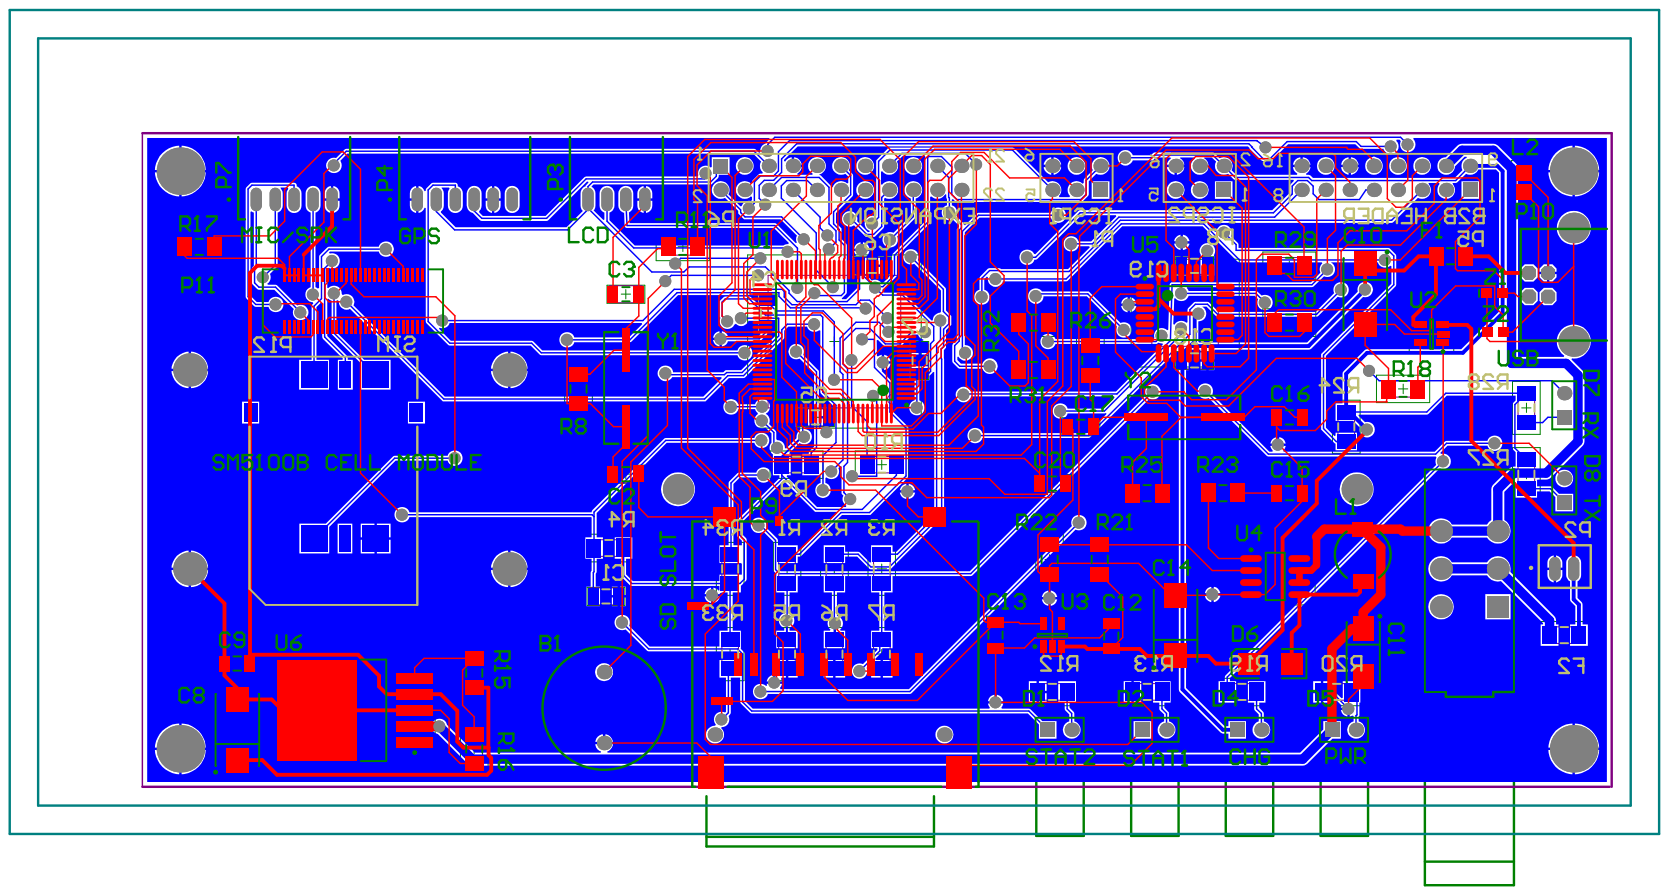
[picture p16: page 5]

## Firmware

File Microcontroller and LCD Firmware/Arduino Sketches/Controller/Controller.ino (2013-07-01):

#include <TinyGPS.h>
#include <SPI.h>
#include <SD.h>

#define SOFTWARE_VERSION "0.2"
#define COMMAND_DELIMITER '\n'
#define GPSUART Serial3
#define CELLUART Serial2
#define LCDUART Serial1
#define PCUART Serial
#define GPSBAUD 4800
#define LCDBAUD 115200
#define CELLBAUD 9600
#define PCBAUD 115200
#define PT_SWITCH_TO_READ_DELAY 1
#define PT_OFFSET 512
#define BATT_VOLTAGE_COEFF 5.0/1024.0
#define NUM_THERMISTOR_SAMPLES_TO_AVG 1000

#define STARTUP_BEEP 1
#define RUN_COMPLETE_BEEP 2
#define ERROR_BEEP 3
#define ASSAY_START_BEEP 4

//digital output control pins
const int heaterControlPin =  35;
const int lightControlPin =  34;
const int stat1LEDPin = 37;
const int stat2LEDPin = 36;
const int buzzerPin = 33;

const int sdCSPin = 8;
const int sdCDPin = 7;
const int sdWPPin = 6;
const int sdSCKPin = 13;
const int sdMISOPin = 12;
const int sdMOSIPin = 11;

//pd address pins
const int U2OutPin = 22;
const int U4OutPin = 23;
const int U5OutPin = 24;
const int A0OutPin = 25;
const int A1OutPin = 26;
const int A2OutPin = 27;
const int A3OutPin = 28;
const int A4OutPin = 29;
//analog input pins
const int batteryInPin = A3;
const int thermistorInPin = A1;
const int phototransistorInPin = A2;

//gps state
float gps_latitude, gps_longitude, gps_altitude;
int gps_year;
byte gps_month, gps_day, gps_hour, gps_minute, gps_second, gps_hundredths;
//TinyGPS gps;

//SD card
boolean sd_card_present = 0;

//heater state
float heater_coeff = 1.0383; //degree C / digital val
float heater_offset = -529.97; //deg C
float heater_tolerance = 0.1;
float heater_sp = 0;
float heater_temp = 0;
boolean heater_on = 0;

//lights state
int lights_level;

//uart state
static String uart_buffer;
static String lcd_buffer;

//TODO: all of these initializations should probably go in a reset() fxn
//pt state
int pt_wellNum = 0;
int pt_numSamplesToAverage = 100;

//controller state
float batt_voltage = 0.0;
int freerun_mode = 0;
int lcd_echo_mode = 0;
int poll_single_well_mode = 0;
int start_well = 1;
int stop_well = 96;
float low_battery_warning = 3.5;

String assay_name = "test_1";
int assay_numrunsteps = 6000;
int assay_numstabilizesteps = 10;
int assay_timestep = 2000;
float assay_heater_sp = 60;
int assay_lights_level = 1;
int assay_state = 0;
int assay_step = 1;
int assay_startwell = 1;
int assay_stopwell = 96;

/* Initializes all the peripherals and runs through a test sequence */
void setup() {
  setupLights();  
  setupHeater();
  setupPCInterface();
  setupLCD();
  setupGPS();
  setupCell();
  setupSDCard();
  setupPhototransistors();
  pinMode(stat1LEDPin, OUTPUT);    
  pinMode(stat2LEDPin, OUTPUT); 
  pinMode(buzzerPin, OUTPUT); 
  
  Serial.println("BioPOETS LAMP Assay System");
  beep(STARTUP_BEEP);
  testLights();
  digitalWrite(stat1LEDPin, HIGH);
  delay(200);
  digitalWrite(stat1LEDPin, LOW);
  delay(200);
  digitalWrite(stat2LEDPin, HIGH);
  delay(200);
  digitalWrite(stat2LEDPin, LOW);
  delay(200);

  //this sends out all the initial state variables to the PC
  getControllerState();
  getGPSState();
  getHeaterState();
  getLightsState();
  getPhototransistorsState();   
}

/* Main program loop */
void loop()
{
  //in the idle state, the sytem continuously queries all the components and streams data to the PC
  //when an assay is run, it is triggered through the UART/LCD.
  pollUART();  
  pollLCD();   
  if (assay_state>0)
    runAssay();
  else if (freerun_mode==1) { 
    pollAllPhototransistors();      
  } 
  else {
    //these polling functions run continuously, even when an assay isn't being run
    pollController();
    pollHeater();  
    pollGPS();      
  }
}

/* runs through the steps of an assay and transmits data to PC for recording */
void runAssay() {
  //set system state
  //state 0 = no assay running
  static unsigned long start_time;
  static unsigned long temp_time;  //todo: redo this so it's an interrupt or something...and have heater PID going at faster loop rate
  if (assay_state>1) { //these 3 numbers mark the beginning of each datapoint
    Serial.print("assay_time "); Serial.println(millis() - start_time);  
    Serial.print("assay_state "); Serial.println(assay_state);
    Serial.print("assay_step "); Serial.println(assay_step); //this should be the keyword that starts a new row...

    LCDUART.write(0xD7);
    LCDUART.print("04");
    LCDUART.print(millis() - start_time);
    LCDUART.write(0x00); 
    
    LCDUART.write(0xD7);
    LCDUART.print("05");
    switch (assay_state) {
      case 0:  LCDUART.print("IDLE"); break;
      case 1:  LCDUART.print("SETUP"); break; 
      case 2:  LCDUART.print("WARMING"); break; 
      case 3:  LCDUART.print("STABILIZE"); break; 
      case 4:  LCDUART.print("RUN"); break; 
      case 5:  LCDUART.print("SHUTDWN"); break;     
    }  
    LCDUART.write(0x00); 
    
    LCDUART.write(0xD7);
    LCDUART.print("06");
    LCDUART.print(assay_step);
    LCDUART.write(0x00); 
  
  }
  switch (assay_state) {
    case 1: //setup
      heater_sp = assay_heater_sp;
      start_well = assay_startwell;
      stop_well = assay_stopwell;
      assay_state = 2;
      assay_step = 1;        
      start_time = millis();
      Serial.print("assay_begin\n"); //signal that the assay is starting and do a dump of all the system state...this will go at top of file
      digitalWrite(stat1LEDPin,HIGH);
      beep(ASSAY_START_BEEP);
      getControllerState();
      getGPSState();
      getHeaterState();
      getLightsState();
      getPhototransistorsState();       
      break;  
    case 2: //warming up
      if (getTempOK()) {
        assay_state = 3;
        beep(ASSAY_START_BEEP);
      }
      break;    
    case 3: //stabilizing the amplifier
      temp_time = millis();
      setLights(assay_lights_level);
      pollAllPhototransistors();
      setLights(0);
      temp_time = assay_timestep - (millis() - temp_time);
      if (temp_time>0)
        delay(temp_time);

      if (assay_step==assay_numstabilizesteps) {
        assay_state = 4;
        beep(ASSAY_START_BEEP);
      }
      assay_step++;      
      break;
    case 4: //recording data
      temp_time = millis();
      setLights(assay_lights_level);
      pollAllPhototransistors();
      setLights(0);
      temp_time = assay_timestep - (millis() - temp_time);
      if (temp_time>0)
        delay(temp_time);
      if (assay_step==(assay_numrunsteps+assay_numstabilizesteps))
        assay_state = 5;
      assay_step++;  
      break;
    case 5: //shutdown
      setLights(0);
      heater_sp = 0;
      assay_state = 0;
      getControllerState();
      getGPSState();
      getHeaterState();
      getLightsState();
      getPhototransistorsState(); 
      digitalWrite(stat1LEDPin,LOW);
      beep(RUN_COMPLETE_BEEP);
      Serial.print("assay_end\n");      
      break;
  }   

  pollController();
  pollHeater();  
}

void pollController() {
  batt_voltage = analogRead(batteryInPin)*BATT_VOLTAGE_COEFF;  
  if (batt_voltage<low_battery_warning)
    digitalWrite(stat2LEDPin,HIGH);
  else
    digitalWrite(stat2LEDPin,LOW);
    
  Serial.print("batt_voltage "); Serial.println(batt_voltage);  
 
  LCDUART.write(0xD7);
  LCDUART.print("07");
  LCDUART.print(batt_voltage);
  LCDUART.write(0x00);    
}

void getControllerState() {
  pollController();
  Serial.print("firmware_ver "); Serial.println(SOFTWARE_VERSION);
  Serial.print("assay_name "); Serial.println(assay_name); 
  Serial.print("assay_numrunsteps "); Serial.println(assay_numrunsteps);
  Serial.print("assay_numstabilizesteps "); Serial.println(assay_numstabilizesteps);
  Serial.print("assay_timestep "); Serial.println(assay_timestep);
  Serial.print("assay_heater_sp "); Serial.println(assay_heater_sp);
  Serial.print("assay_lights_level "); Serial.println(assay_lights_level);
  Serial.print("assay_startwell "); Serial.println(assay_startwell);
  Serial.print("assay_stopwell "); Serial.println(assay_stopwell);
  Serial.print("assay_state "); Serial.println(assay_state);
  
  LCDUART.write(0xD7);
  LCDUART.print("02");
  LCDUART.print(assay_name);
  LCDUART.write(0x00);  
  
}

void beep(int beepType) {

 switch (beepType) {
  case 1: //startup beep
    digitalWrite(buzzerPin, HIGH);
    delay(50);
    digitalWrite(buzzerPin, LOW);
    delay(50);
    digitalWrite(buzzerPin, HIGH);
    delay(50);
    digitalWrite(buzzerPin, LOW);
    break;
  case 2: //assay complete beep
    digitalWrite(buzzerPin, HIGH);
    delay(1000);
    digitalWrite(buzzerPin, LOW);
    delay(1000);
    digitalWrite(buzzerPin, HIGH);
    delay(1000);
    digitalWrite(buzzerPin, LOW);
    delay(1000);
    digitalWrite(buzzerPin, HIGH);
    delay(1000);
    digitalWrite(buzzerPin, LOW);
    delay(1000);    
    break;
  case 3:
    digitalWrite(buzzerPin, HIGH);
    delay(20);
    digitalWrite(buzzerPin, LOW);
    delay(20);
    digitalWrite(buzzerPin, HIGH);
    delay(20);
    digitalWrite(buzzerPin, LOW);
    delay(20);
    digitalWrite(buzzerPin, HIGH);
    delay(20);
    digitalWrite(buzzerPin, LOW);
    delay(500); 
    digitalWrite(buzzerPin, HIGH);
    delay(20);
    digitalWrite(buzzerPin, LOW);
    delay(20);
    digitalWrite(buzzerPin, HIGH);
    delay(20);
    digitalWrite(buzzerPin, LOW);
    delay(20);
    digitalWrite(buzzerPin, HIGH);
    delay(20);
    digitalWrite(buzzerPin, LOW);
    delay(500); 
    digitalWrite(buzzerPin, HIGH);
    delay(20);
    digitalWrite(buzzerPin, LOW);
    delay(20);
    digitalWrite(buzzerPin, HIGH);
    delay(20);
    digitalWrite(buzzerPin, LOW);
    delay(20);
    digitalWrite(buzzerPin, HIGH);
    delay(20);
    digitalWrite(buzzerPin, LOW);
    delay(500);    
    break;   
 case 4: //assay start beep
    digitalWrite(buzzerPin, HIGH);
    delay(500);
    digitalWrite(buzzerPin, LOW);    
 }
}

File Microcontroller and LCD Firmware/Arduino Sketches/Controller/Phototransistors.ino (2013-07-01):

/*address lines are:
  Array Position: 0  1  2  3  4  5  6  7
  LAMP Board:     U2 U4 U5 A0 A1 A2 A3 A4
  P1 Pin:         1  2  3  4  5  6  7  8
  Arduino IO Pin: 4  5  6  7  8  9  10 11
  
  Note that enable lines are active low, while address lines are active high.
  
  */

/* these are the addresses of each phototransistor */  
const int address[] = 
{ 
B11100000,  //D0
B10101011,  //D1
B10100111,  //D2
B10100011,  //D3
B01101111,  //D4
B01101011,  //D5
B01100111,  //D6
B01100011,  //D7
B01110000,  //D8
B01110101,  //D9
B01111000,  //D10
B01111100,  //D11
B10110000,  //D12
B10101010,  //D13
B10100110,  //D14
B10100010,  //D15
B01101110,  //D16
B01101010,  //D17
B01100110,  //D18
B01100010,  //D19
B01110001,  //D20
B01110100,  //D21
B01111001,  //D22
B01111101,  //D23
B10110001,  //D24
B10101001,  //D25
B10100101,  //D26
B10100001,  //D27
B01101101,  //D28
B01101001,  //D29
B01100101,  //D30
B01100001,  //D31
B01110010,  //D32
B01110110,  //D33
B01111010,  //D34
B01111110,  //D35
B10110010,  //D36
B10101000,  //D37
B10100100,  //D38
B10100000,  //D39
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
};

void setupPhototransistors() {
  pinMode(U2OutPin, OUTPUT);  
  pinMode(U4OutPin, OUTPUT); 
  pinMode(U5OutPin, OUTPUT); 
  pinMode(A0OutPin, OUTPUT); 
  pinMode(A1OutPin, OUTPUT); 
  pinMode(A2OutPin, OUTPUT); 
  pinMode(A3OutPin, OUTPUT); 
  pinMode(A4OutPin, OUTPUT); 
  setWell(0);
}

int setWell(int wellNum) {
  digitalWrite(U2OutPin,((address[wellNum]&B10000000)!=0)?HIGH:LOW);
  digitalWrite(U4OutPin,((address[wellNum]&B01000000)!=0)?HIGH:LOW);
  digitalWrite(U5OutPin,((address[wellNum]&B00100000)!=0)?HIGH:LOW);
  digitalWrite(A4OutPin,((address[wellNum]&B00010000)!=0)?HIGH:LOW);
  digitalWrite(A3OutPin,((address[wellNum]&B00001000)!=0)?HIGH:LOW);
  digitalWrite(A2OutPin,((address[wellNum]&B00000100)!=0)?HIGH:LOW);
  digitalWrite(A1OutPin,((address[wellNum]&B00000010)!=0)?HIGH:LOW);
  digitalWrite(A0OutPin,((address[wellNum]&B00000001)!=0)?HIGH:LOW); 
  pt_wellNum = wellNum;
}

void pollAllPhototransistors() {
  long collector;
  float average;
  for (int i=start_well;i<=stop_well;i++) {
    setWell(i);
    delay(PT_SWITCH_TO_READ_DELAY);
    collector = 0;
    for (int j=0;j<pt_numSamplesToAverage;j++) {
      collector += analogRead(phototransistorInPin); 
    }
    average = ((float)collector)/((float)pt_numSamplesToAverage) - PT_OFFSET;
    Serial.print("pt "); Serial.print(i); Serial.print(" "); Serial.println(average);
  
    char add[3];
    char val[5];
   
    sprintf(add,"%02X",i);
    sprintf(val,"%04X",(int)average); 
    LCDUART.write(0xD6);
    LCDUART.print(add);
    LCDUART.print(val);
    LCDUART.write(0x00); 
    Serial.println("test");  
    Serial.println(add);
    Serial.println(val);
    Serial.println("test");    
  }  
}

void pollSinglePhototransistor() {
  long collector;
  float average;
  collector = 0;
  for (int j=0;j<pt_numSamplesToAverage;j++) {
    collector += analogRead(phototransistorInPin); 
  }
  average = ((float)collector)/((float)pt_numSamplesToAverage) - PT_OFFSET;
  Serial.print("pt "); Serial.print(pt_wellNum); Serial.print(" "); Serial.println(average);  
}

void getPhototransistorsState() {
    Serial.print("pt_wellnum "); Serial.println(pt_wellNum);
    Serial.print("pt_numsamplestoavg "); Serial.println(pt_numSamplesToAverage);  
}

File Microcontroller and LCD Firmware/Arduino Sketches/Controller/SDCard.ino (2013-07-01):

void setupSDCard() {
  pinMode(sdCSPin, OUTPUT);     
  pinMode(sdCDPin, INPUT);    
  pinMode(sdWPPin, INPUT);   

  //I screwed up and accidentally connected these instead. note that on the board I've added jumpers to the correct SCK/MISO/MOSI pins (51, 52, 53)
  pinMode(sdSCKPin, INPUT);   
  pinMode(sdMISOPin, INPUT);    
  pinMode(sdMOSIPin, INPUT);     

  // make sure that the default chip select pin is set to
  // output, even if you don't use it:
  pinMode(53, OUTPUT);
 
  // see if the card is present and can be initialized:
  if (!SD.begin(sdCSPin)) {
    Serial.println("SD Card failed or not present");
    sd_card_present = false;
    return;
  }
  Serial.println("SD card initialized."); 
  sd_card_present = true;
 
  sdWrite("TEST");
}

//writes a string to the SD card
//TODO: check files on card and sequentially number new files
//TODO: whatever gets sent to PC should also get sent to SD card (log file)
void sdWrite(String txt) {
  File dataFile = SD.open("microbar.log", FILE_WRITE);  
  // if the file is available, write to it:
  if (dataFile) {
    dataFile.print(txt);
    dataFile.close();
  }  
  // if the file isn't open, pop up an error:
  else {
    Serial.println("error opening datalog.txt");
  }  
  
}
